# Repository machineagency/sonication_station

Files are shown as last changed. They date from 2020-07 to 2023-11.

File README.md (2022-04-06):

If you're looking for a standard operating procedure, check out the [quickstart](docs/quickstart.md).

## Intro
This project wraps a python interface around the existing Duet 3 Socket Interface, turning Jubilee into a plate handling lab automation device for sonication.

## Connecting to Jubilee
There are two ways to connect to Jubilee and execute code: (1) locally and (2) with a separate PC over a network connection.

They look like this:

### Local Connection
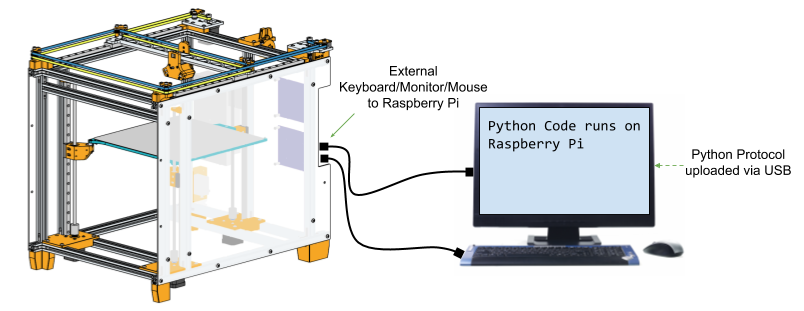
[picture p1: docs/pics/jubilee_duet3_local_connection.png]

In this mode, the Python protocol runs on the Raspberry Pi attached to the machine. It is recommended for production use.

### Closed Network Connection
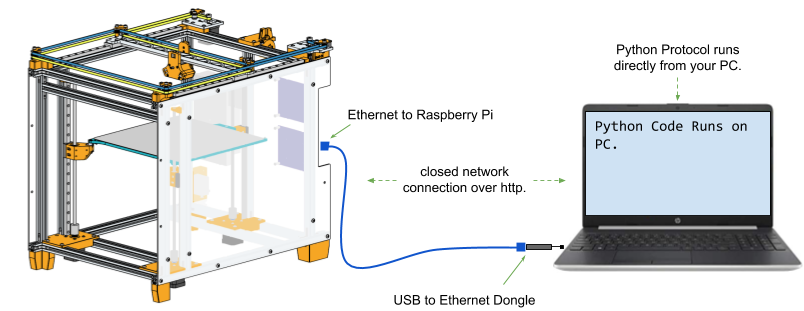
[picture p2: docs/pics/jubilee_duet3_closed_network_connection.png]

In this mode, the Python protocol runs on a separate pc with this software package installed. It is useful for testing but not recommended for production.

When running the machine in this mode, note that turning off your PC or losing the network connection will halt the machine mid-execution.
Furthermore, a laggy network connection will cause the machine to lag.
To avoid these issues in production, we recommended that running the protocol locally (on the Raspberry Pi) instead of using an arbitrary PC on the same network.

## Installation
If you are running this code locally, clone this repository onto Jubilee's attached Raspberry Pi. If you are running it over a network connection, clone it onto your PC.

Then, from within this directory (the one with this README in it), install the project via pip with ....
```
pip3 install -e .
```

Now you can spin up a connection to Jubilee by importing the driver.

## Conventions
Looking top-down at the plate, plates are indexed as follows:

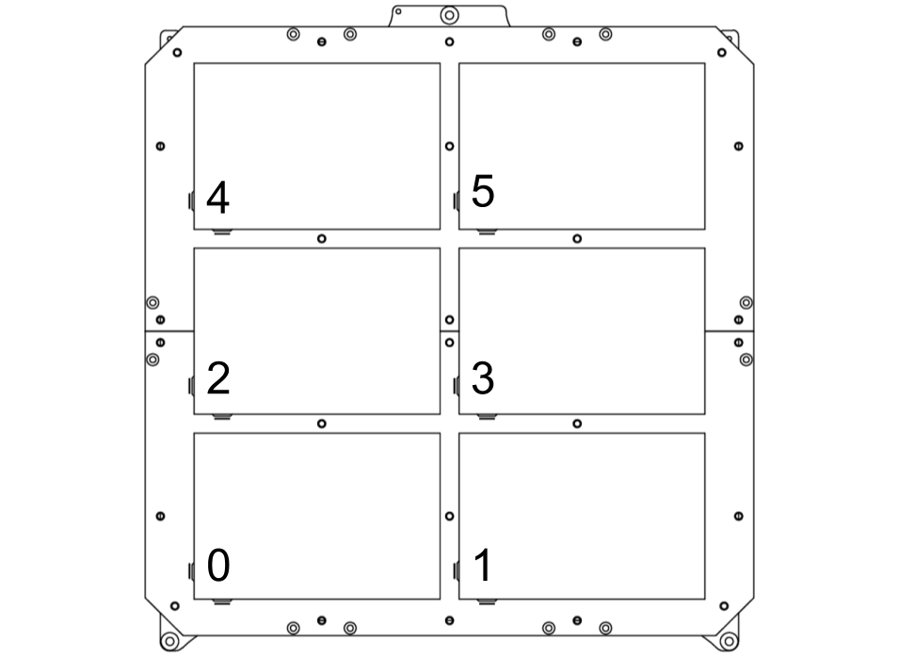
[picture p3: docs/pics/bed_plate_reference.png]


### Starting Machine State
When Jubilee is first powered up, it will need to first home all axes. You must issue this command yourself. To home, the deck must be clear of all labware.
After homing, you may populate the deck and execute protocols can be run. You only need to home once when Jubilee is first turned on, or once after any situation where the machine has lost it's position (from an event like a crash).

### Machine Pre-Protocol Setup
Once the machine is homed, you can then load labware into the machine. You will need to configure the machine with the labware you add. This can be done interactively in **prompt mode** with the *setup_plate* command. After configuring, the deck configuration can be saved to a file. If the same labware is used for a different protocol, you can reuse this file instead of reconfiguring the deck.

### Ending Machine State
All tools must be put away before Jubilee is powered off. This is the default behavior if you run the code inside a *with* statement. In any situation where the Jubilee was powered off in an emergency, you must remove any active tools on Jubilee's carriage before powering it back on.

## API
There are 3 ways of interacting with the machine:
(1) directly through a python script,
(2) interactively through a command prompt, and
(3) procedurally with predefined protocol.

## Python Script Mode
After installing this package with pip, you should be able to simply import it in python:

If you are running the code locally, the code will look like this:
```python
from sonication_station.sonication_station import SonicationStation
with SonicationStation() as jubilee:
    jubilee.sonicate_well(0, 'A', 0, 3, 10, False)
```
If you are running the code over a network from a separate PC, the code may look like this:
```python
from sonication_station.sonication_station import SonicationStation
with SonicationStation(address="192.168.1.2") as jubilee:
    jubilee.sonicate_well(0, 'A', 0, 3, 10, False)
```
Here the above *address* argument is the ip address of Jubilee as it appears on your network.

## Prompt (Maintenance) Mode
You can interactively control Jubilee through a custom prompt.
To interact with the prompt, spin it up from the python shell with:

```python
from sonication_station.sonication_station import SonicationStation
with SonicationStation() as jubilee:
    jubilee.cmdloop()
```

or, from the command line:

```
sudo path/to/sonication_station/sonication_station.py
```

This will drop you into an interactive prompt that looks like this:
```

  ____              _           _   _               ____  _        _   _             
 / ___|  ___  _ __ (_) ___ __ _| |_(_) ___  _ __   / ___|| |_ __ _| |_(_) ___  _ __  
 \___ \ / _ \| '_ \| |/ __/ _` | __| |/ _ \| '_ \  \___ \| __/ _` | __| |/ _ \| '_ \ 
  ___) | (_) | | | | | (_| (_| | |_| | (_) | | | |  ___) | || (_| | |_| | (_) | | | |
 |____/ \___/|_| |_|_|\___\__,_|\__|_|\___/|_| |_| |____/ \__\__,_|\__|_|\___/|_| |_|
                                                                                     

>>> 

```
This mode lets you input commands one at a time.

In this mode you can:

* home the machine
* execute movement commands
* execute sonication commands
* pickup and park tools
* interactively set the location/type of a new well plate
* control the machine with the keyboard arrow keys
setup the machine and execute commands serially. This interface is useful for adding to the plate inventory.

To see the list of supported commands, press TAB twice. This mode also supports TAB completion, that is, if you start typing a command and press TAB twice, the prompt will either attempt to auto-complete any possibilities or show you a list of possible completions.
To get help on any command, simply type:

```
>>> help command_name_here
```

## Protocol Mode
This method is for invoking predefined protocol. Protocol mode may be useful for generating a series of plate operations programmatically from another program and then simply executing them on the Sonication Station. Protocols consist of a series of sonication commands executed sequentially.

Running the machine in protocol mode is simply a matter of telling the machine to read a predefined protocol file.
```python
# Assume that Jubilee is both homed and populated with the correct labware for this protocol.
from sonication_station.sonication_station import SonicationStation
with SonicationStation() as jubilee:
    jubilee.execute_protocol_from_file("/path/to/protocol_file.json")
```

### Protocol API
Under the hood, a protocol file is a json file. A sample protocol looks like this:
```json
{
   "protocol": [
       {
           "operation": "sonicate_well",
           "specs": {
               "deck_index": 5,
               "row_letter": "A",
               "column_index": 1,
               "plunge_depth": 10.0,
               "seconds": 3.0,
               "autoclean": false
           }
       },
       {
           "operation": "sonicate_well",
           "specs": {
               "deck_index": 5,
               "row_letter": "A",
               "column_index": 2,
               "plunge_depth": 10.0,
               "seconds": 3.0,
               "autoclean": false
           }
       }
   ]
}
```
Here, the protocol contains one important field *protocol*, which is a list of operations that will be executed sequentially.
So far, only one operation **sonicate_well**, is implemented. the options are as follows:
* **deck_index:** the deck index of the plate
* **row_letter:** the row index on the plate, indicated by letter
* **column_index:** the column indicated by integer
* **plunge_depth:** the depth to plunge the sonicator into the glassware as measured from the top of the glassware
* **seconds:** time in seconds to run the sonicator
* **autoclean**: (boolean), whether or not to run a predefined cleaning protocol.

Note that if **autoclean** is set to true, a cleaning protocol must be defined in the machine configuration. Cleanin protocols can also be defined in prompt mode.

## Deck Configuration
Before running a protocol, Jubilee's deck must be configured with the labware that the protocol needs. Specifically, Jubilee needs to know:
* for each piece of labware
    * the well count (12 \[scintillation vile holder\], 48, 96, etc)
    * the XY location of the labware
    * the deck slot number
    * the height of the labware
* a minimum height at which all tools can safely travel over all labware currently loaded on the deck (the *safe_z* height).

This configuration must be done in **prompt mode**.

### Safe Z Height
The *safe_z* height is the height at which the tip of any tool can safely clear the tallest labware without crashing into it. It is defined in mm as the distance of the active tool tip and the deck plate surface.

If the machine is homed, you can measure the current tool tip height by issuing the *position* command.
```
>>> position
[150.0, 150.0, 65.0]
>>> 
```
Here the XYZ coordinates are 150, 150, 65mm respectively.

You set the *safe_z* height in **prompt mode** like so:
```
>>> safe_z z=65
```

You can read back the *safe_z* by simply entering *safe_z* without arguments
```
>>> safe_z
65
>>>
```

### Plate Setup
You can add a piece of labware into Jubilee's configuration by running the *setup_plate* command. This will drop you into an interactive session where the machine will walk you through the setup.

When the machine is configured, you can save your configuration to a file with *save_deck_configuration*. That way, you can run the same protocol again without having to redo this (somewhat tedious) setup.

### Acknowledgements
This work was partially supported by the  University of Washington (UW) Molecular Engineering Materials Center (MEM-C)

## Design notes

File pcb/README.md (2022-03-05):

# Sonicator PCB

This PCB attaches on top of the Raspberry Pi enabling its GPIOs to control the Sonicator.

## Fabrication

To make this pcb, you'll need to send files (usually gerbers) out to a PCB Fab house of your choice.
Here are some options:

* [OSH Park](https://oshpark.com/) will actually natively accept **.kicad\_pcb** files directly. (This is probably the easiest option.)
    * [instructions for gerber generation](https://docs.oshpark.com/design-tools/kicad/generating-kicad-gerbers/)
* [PCBWay](http://pcbway.com/)
    * [instructions for gerber generation](https://www.pcbway.com/blog/help_center/Generate_Gerber_file_from_Kicad.html)
* Bay Area Circuits has a No-Silk-No-Soldermask 24-hour [Bare Bones Special](https://bayareacircuits.com/prototype-printed-circuit-boards-pcbs/) for time crunched prototypes.

## Assembly

This PCB can be assembled by hand with some tweezers, a microscope (or cheap microscope webcam), and, optionally, a stencil.
Parts will need to be ordered from the BOM.
(You can regenerate the BOM from the native Kicad files.)

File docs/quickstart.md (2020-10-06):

# Quickstart

The General Standard Operating Procedure for running a protocol on Jubilee:

## Standard Operating Procedure for Production Use
Assumes procedures will run locally on the attached Raspberry Pi.

1. Power on the machine without labware
1. Home the machine
1. If code was written elsewhere, upload it to the machine with a USB drive.
1. Configure the deck plate or use an existing deck plate configuration file.
1. Populate the deck with labware
1. Either:
    1. Execute one or more sonication operations in manual mode
    1. Execute one or more python scripts
    1. Execute one or more json protocol files
1. Ensure that all tools are put away
1. Remove all labware from the machine
1. Power off the machine

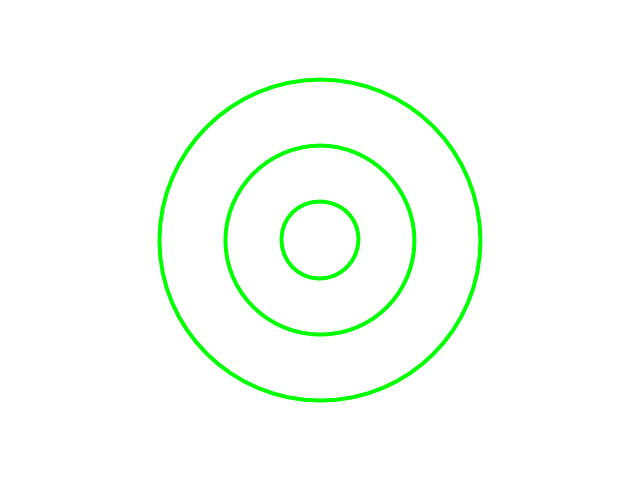
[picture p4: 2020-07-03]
sonication_station/web_video_feed/overlay.png

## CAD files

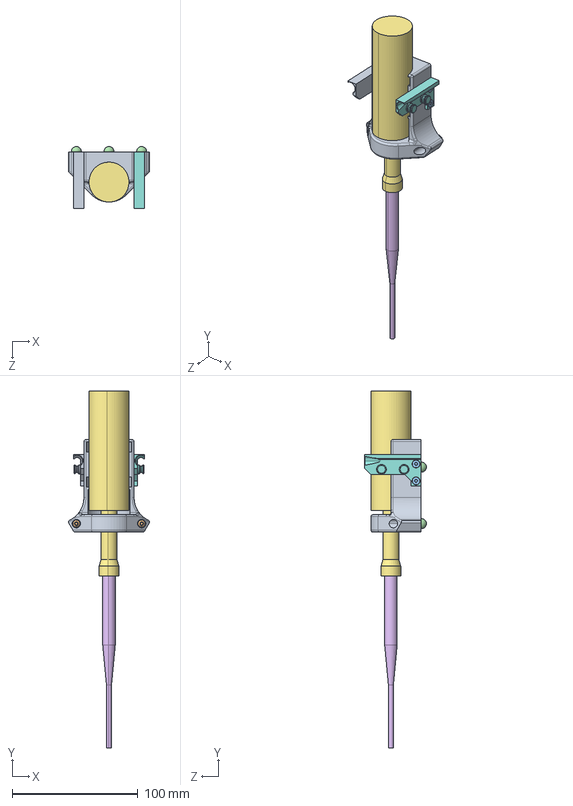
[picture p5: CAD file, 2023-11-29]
tools/q125_sonicator_tool/step/sonicator_tool_assembly.STEP
64.4 x 284.1 x 49.3 mm
sonicator_base_tool_plate_tool plate
wedge_plate
m3_6mm_flathead_screw_92125A126_92125A126 x 7
m3_threaded_ball x 3
m3_heat_set_insert_94180A331_94180A331 x 3
q125_sonicator_head
sonicator_tool_wing_Standard Right Tool Wing
sonicator_tool_wing_Standard Left Tool Wing
m3_6mm_buttonhead_screw_92095A179_92095A179 x 3

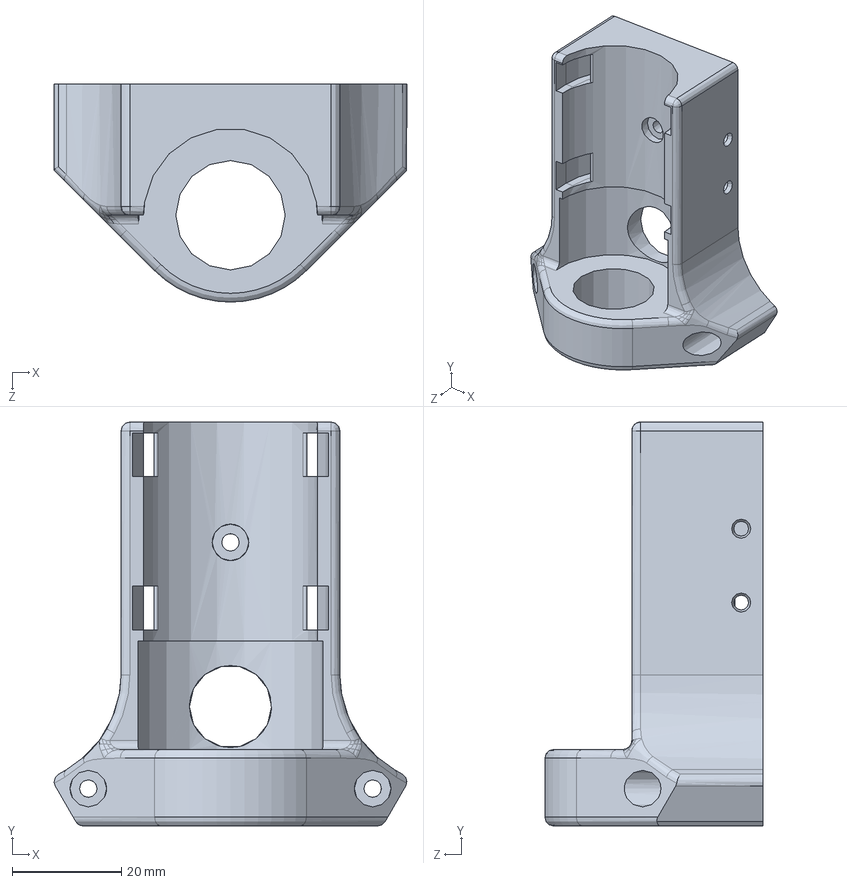
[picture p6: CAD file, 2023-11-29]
tools/q125_sonicator_tool/solidworks/sonicator_base_tool_plate.SLDPRT
64.5 x 73.8 x 39.9 mm

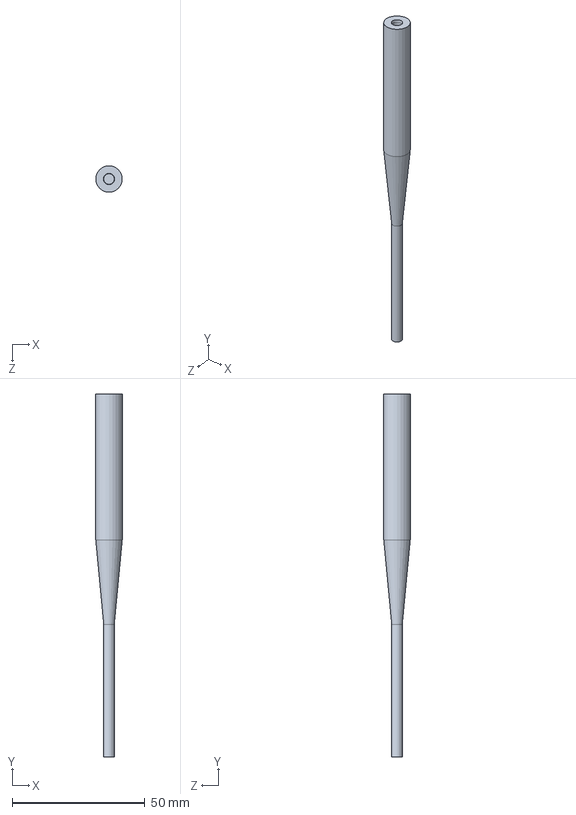
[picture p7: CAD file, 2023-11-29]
tools/q125_sonicator_tool/solidworks/q125_sonicator_head.SLDPRT
10.0 x 136.8 x 10.0 mm

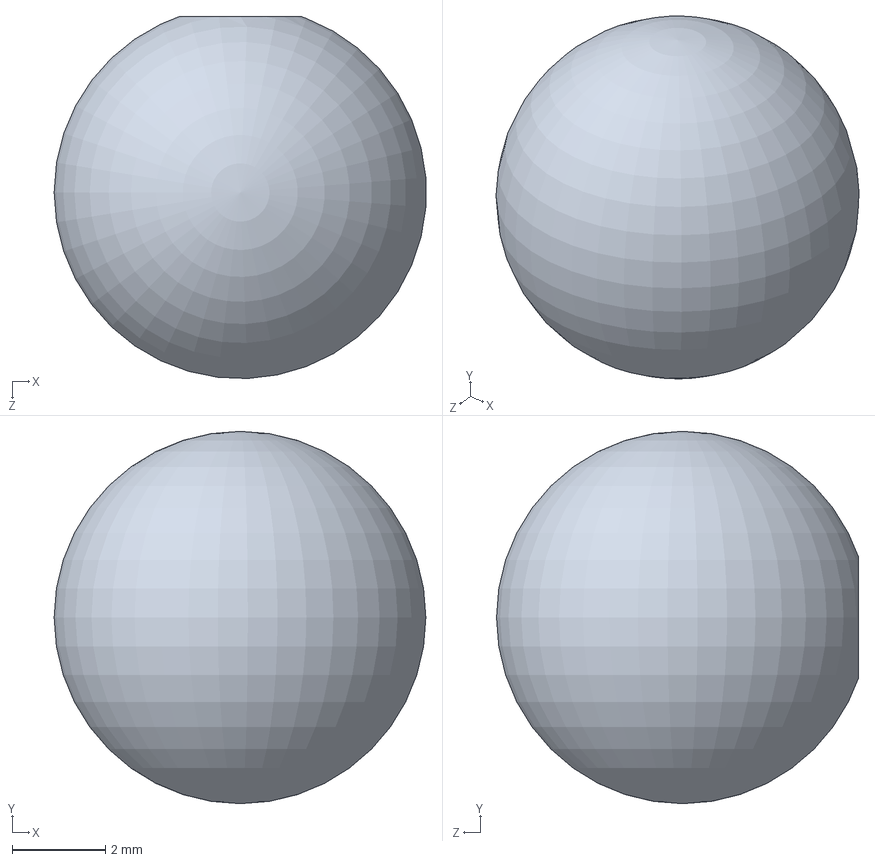
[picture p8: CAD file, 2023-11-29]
tools/q125_sonicator_tool/solidworks/m3_threaded_ball.SLDPRT
7.99 x 8.00 x 7.78 mm

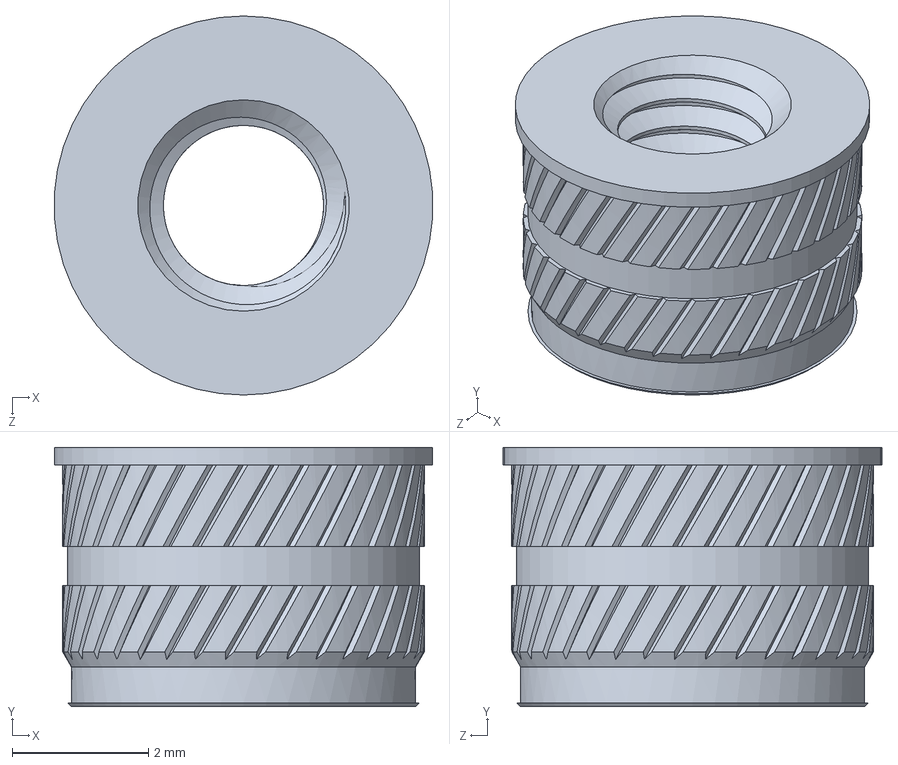
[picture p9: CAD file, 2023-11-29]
tools/q125_sonicator_tool/solidworks/m3_heat_set_insert_94180A331.SLDPRT
5.55 x 3.80 x 5.56 mm

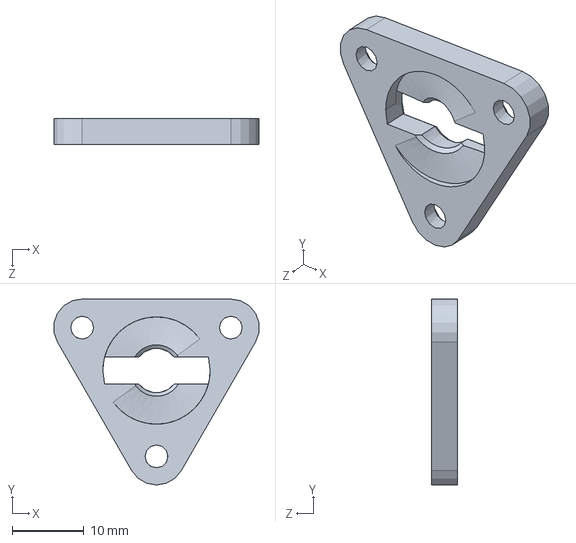
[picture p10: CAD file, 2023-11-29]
tools/q125_sonicator_tool/solidworks/wedge_plate.SLDPRT
28.7 x 26.0 x 3.60 mm

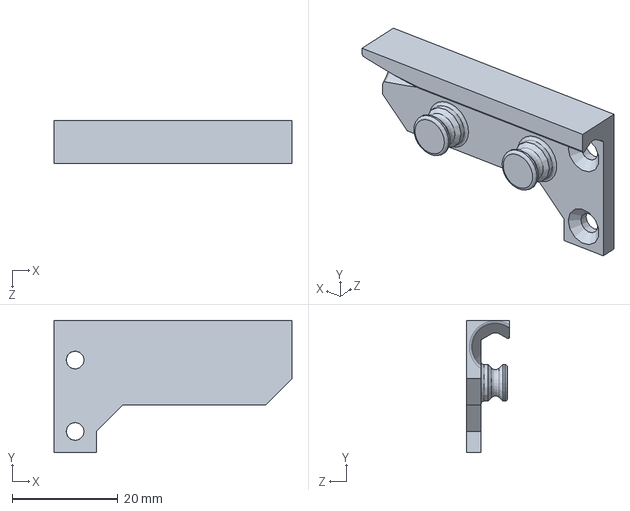
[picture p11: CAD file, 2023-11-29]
tools/q125_sonicator_tool/solidworks/sonicator_tool_wing.SLDPRT
45.0 x 25.0 x 8.20 mm

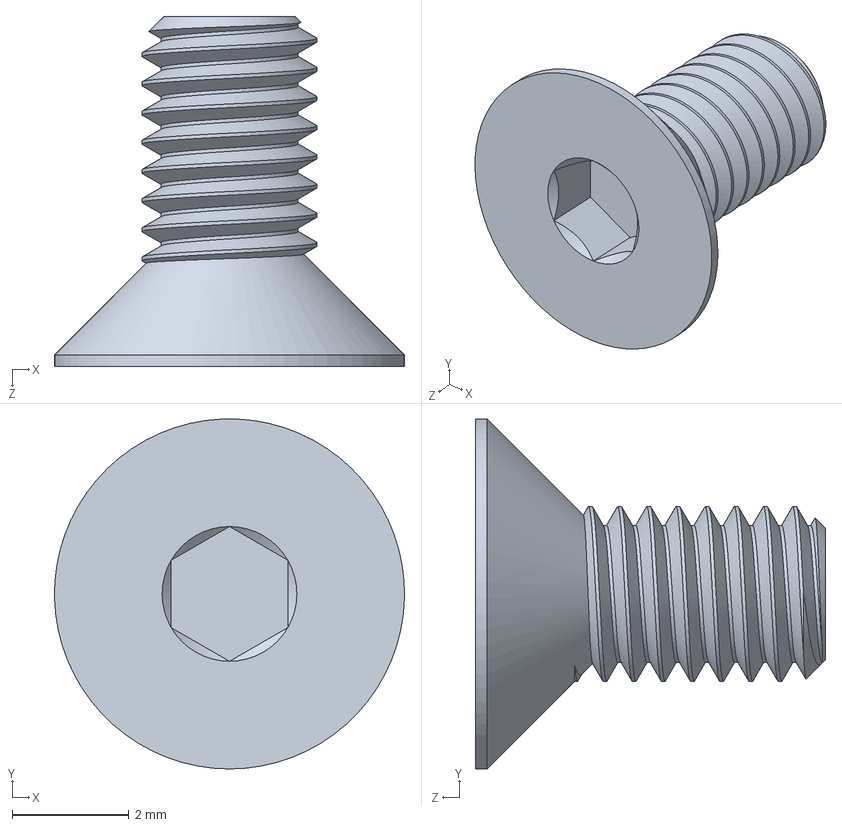
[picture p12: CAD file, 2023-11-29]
tools/q125_sonicator_tool/solidworks/m3_6mm_flathead_screw_92125A126.SLDPRT
6.00 x 6.00 x 6.00 mm

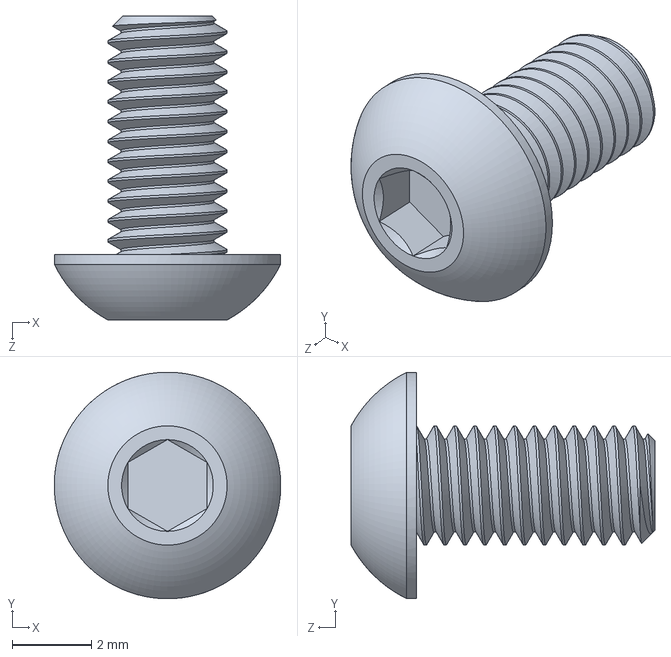
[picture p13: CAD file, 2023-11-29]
tools/q125_sonicator_tool/solidworks/m3_6mm_buttonhead_screw_92095A179.SLDPRT
5.70 x 5.70 x 7.65 mm

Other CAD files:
tools/q125_sonicator_tool/solidworks/sonicator_tool_assembly.SLDASM

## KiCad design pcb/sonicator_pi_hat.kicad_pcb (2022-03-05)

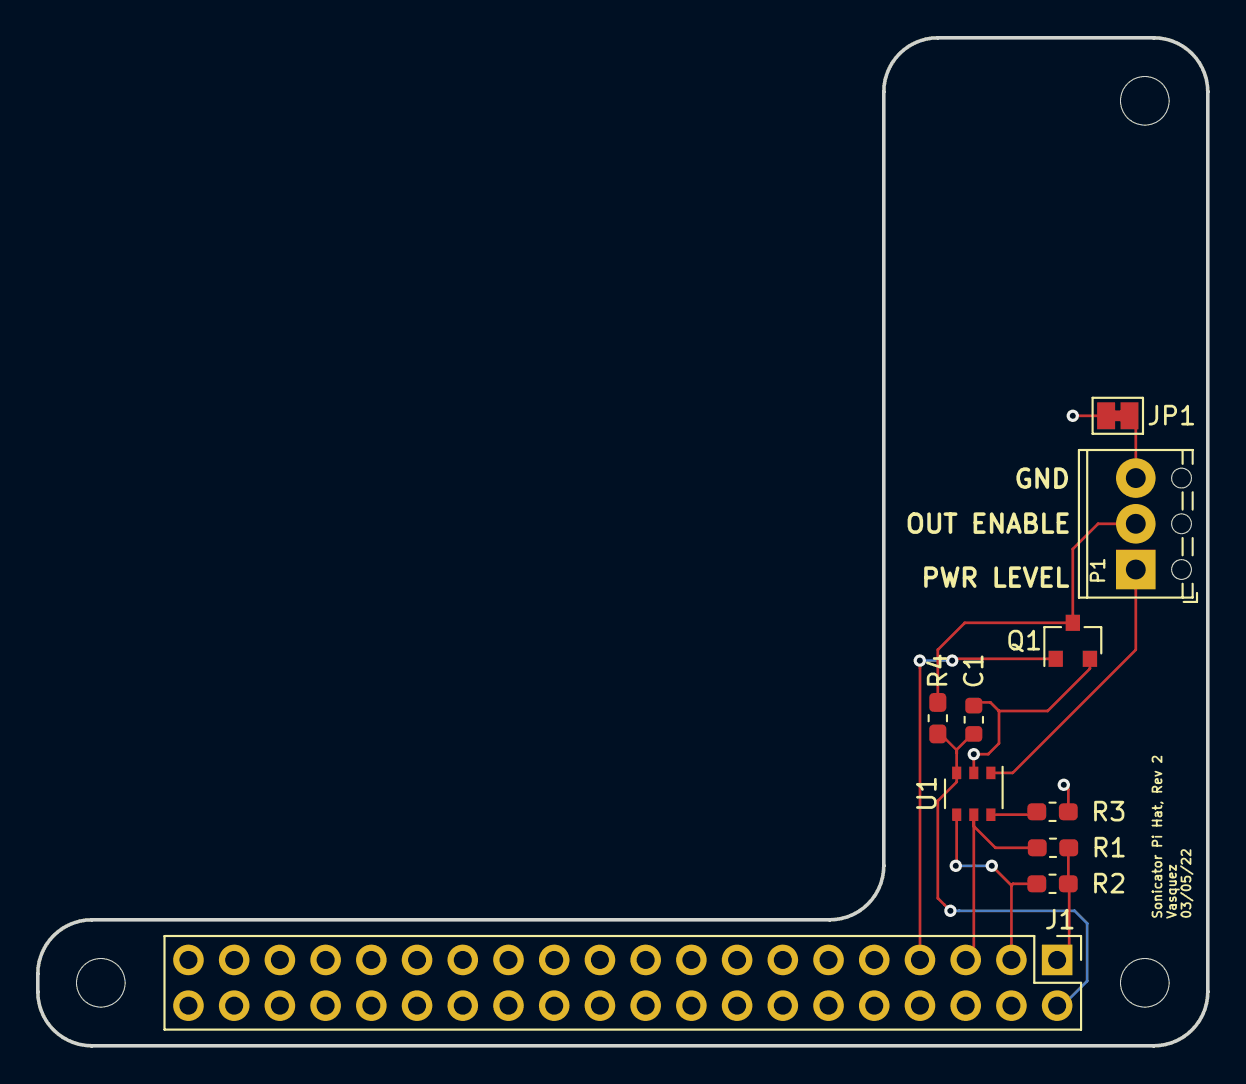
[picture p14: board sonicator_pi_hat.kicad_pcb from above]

Board: 2 copper layers, 65.0 x 56.0 mm, 10 parts (0 on the bottom side), 10 nets.

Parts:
C1: 1uF; C_0603_1608Metric
J1: Raspberry_Pi_2_3; PinHeader_2x20_P2.54mm_Vertical
JP1: Jumper; SolderJumper-2_P1.3mm_Bridged_Pad1.0x1.5mm
P1: 3pos_terminal_block; TerminalBlock_Phoenix_MPT-0,5-3-2.54_1x03_P2.54mm_Horizontal
Q1: 2N7002; SOT-23
R1, R2, R4: 4k7; R_0603_1608Metric_Pad1.05x0.95mm_HandSolder
R3: 10k; R_0603_1608Metric_Pad1.05x0.95mm_HandSolder
U1: MCP4725; TSOP-6_1.65x3.05mm_P0.95mm

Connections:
+3V3: J1.1 (3V3), R1.1, R2.1
+5V: C1.1, J1.2 (5V), R4.1, U1.3 (VDD)
/OUTPUT_ENABLE: P1.2, Q1.3 (D), R4.2
/OUTPUT_PWR_LEVEL: P1.1, U1.1 (VOUT)
GND: C1.2, J1.6 (GND), J1.9 (GND), J1.14 (GND), J1.20 (GND), J1.25 (GND), J1.30 (GND), J1.34 (GND), J1.39 (GND), JP1.1, Q1.2 (S), R3.2, U1.2 (VSS)
GNDPWR: JP1.2, P1.3
unnamed: J1.3 (SDA/GPIO2), R2.2, U1.4 (SDA)
unnamed: J1.5 (SCL/GPIO3), R1.2, U1.5 (SCL)
unnamed: J1.7 (GCLK0/GPIO4), Q1.1 (G)
unnamed: R3.1, U1.6 (A0)

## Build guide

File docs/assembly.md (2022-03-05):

# Machine Assembly

Transforming Jubilee into the Sonication Station requires the addition of some custom hardware and software beyond building the frame.

## Hardware Checklist

### Single Board Computer for SBC Mode
* 32GB SD card
* Raspberry Pi 4, 4GB
* ethernet cable
* [ethernet-to-usb3 adapter](https://www.amazon.com/gp/product/B00M77HMU0)

### Sonicator Tool
* Q125 Sonicator Horn
* Sonicator Probe (various probe sizes, including pn: 4423, pn: 4422, and pn: 4435)
* Sonicator Control PCB, pn: KITVC1025 (20kHz) or pn: KITVC1045 (40kHz)
* Sonicator Wiring Harness
    * 1x [Molex: 0022552102](https://www.digikey.com/en/products/detail/molex/0022552102/303176)
    * 3x [Molex: 0016020086](https://www.digikey.com/en/products/detail/molex/0016020086/467788)
    * 1x [McMaster-Carr: 7243K117](https://www.mcmaster.com/7243K117/) for the sonicator horn wiring
    * 1x [McMaster-Carr: 7243K122](https://www.mcmaster.com/7243K122/) for the sonicator horn wiring

### Camera Tool
* [Sonicator Pi Hat PCB](./pcb)
* [Arducam Lens Board](https://www.amazon.com/gp/product/B013JTY8WY)
* [HDMI Cable](https://www.amazon.com/gp/product/B00Z07JYLE) (flexible, 2m or 6ft)
* [Arducam CSI to HDMI Cable Extension Module](https://www.amazon.com/gp/product/B06XDNBM63)

## Overall Setup

Jubilee will be provisioned in "SBC Mode" and the sonication\_station python package in this repository will be installed on it.
The Sonicator Pi Hat will be attached to the Pi and connected to the Sonicator Control PCB.

## Diagram HERE

## Assembly Instructions
1. Order and populate the [Sonicator Pi Hat](./pcb) PCB.
1. Order the Parts for a Sonicator Tool and a Camera Tool.
1. Install [DuetPi](https://docs.duet3d.com/en/User_manual/Machine_configuration/SBC_setup) OS on the Raspberry Pi
1. Assemble the Sonicator Tool and harness and the camera tool and harness.
1. Connect to the Raspberry Pi, give it internet access, and install the sonication\_station package according to the [instructions](https://github.com/machineagency/sonication_station#installation)
1. Set the XYZ Tool Offsets of the Sonicator and and Jubilee Tool.

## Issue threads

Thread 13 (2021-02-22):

### ISSUE TITLE
Autocleaning needs to have power option exposed during setup_autoclean_protocol

### ISSUE THREAD

**Issue by Antonedw** [machineagency/sonication_station#13]
Expose power option as an input when using **prompt mode**  else leads to error due to missing argument when running protocol.

**Comment by Poofjunior** [comment]
also implemented in this branch. Needs testing.
https://github.com/machineagency/sonication_station/tree/dev/duty_cycle_sonication

**Comment by Poofjunior** [comment]
Ok this looks good!

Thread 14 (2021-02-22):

### ISSUE TITLE
Sonication horn remains on after KeyboardInterrupt in Prompt Mode

### ISSUE THREAD

**Issue by Antonedw** [machineagency/sonication_station#14]
When interrupting a protocol running in prompt mode the sonication horn stays on after the keyboard interruption. The horn stays on to the same setting that was present during the keyboard interruption. Currently, the only way to stop the horn is to turn the entire machine on and off completely.

**Comment by Poofjunior** [comment]
Ok; this looks like it should be a quick fix. Changes are up here in a branch that I should be able to test before the end of the weekend.
https://github.com/machineagency/sonication_station/tree/dev/sonicator_safe_exit

**Comment by Poofjunior** [comment]
Ok this should now be fixed.

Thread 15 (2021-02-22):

### ISSUE TITLE
Duty cycle for sonication horn not present

### ISSUE THREAD

**Issue by Antonedw** [machineagency/sonication_station#15]
The option of the duty cycle is not present as an argument to sonicate_well(). At the moment, a duty (ratio on/off) cycle is achievable by just calling the horn to run in another well, however, the power option to zero or a pause feature is needed.

**Comment by Poofjunior** [comment]
Ok, also implemented, but needs to get tested later.
https://github.com/machineagency/sonication_station/tree/dev/duty_cycle_sonication

**Comment by Poofjunior** [comment]
Ok, this is now implemented. When you run it, you'll get a print message when the sonicator turns on and off. (We can get rid of this if you want.)
```
>>> sonicate_well 0 A 0 15 2.5 1 1 2 autoclean=False
Moving to: (264.055, 200.000)
Sonicating for 2.5 seconds!!
0.00 | Sonicator on.
2.00 | Sonicator off.
2.00 | Sonicator on.
2.50 | Sonicator off.
2.50 | Finished sonicating.
done!
Moving to: (124.250, 79.750)
Sonicating for 3.0 seconds!!
0.00 | Sonicator on.
0.50 | Sonicator off.
1.00 | Sonicator on.
1.50 | Sonicator off.
2.00 | Sonicator on.
2.50 | Sonicator off.
3.00 | Finished sonicating.
done!
Moving to: (96.167, 79.750)
Sonicating for 3.0 seconds!!
0.00 | Sonicator on.
0.50 | Sonicator off.
1.00 | Sonicator on.
1.50 | Sonicator off.
2.00 | Sonicator on.
2.50 | Sonicator off.
3.00 | Finished sonicating.
done!
```

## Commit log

2020-06-21 updating completion to print in columns
2020-07-04 launching/killing camera feed works
2020-07-05 adding general case toolchange macros for tools with very different heights
2020-07-11 got sleep-until-next-thread-update working
2020-08-11 hid extraneous camera output
2020-08-27 camera pickup turns on camera
2020-11-06 exposing sonicator power level
2020-12-02 exposing power level for config mode.
2022-03-05 adding kicad pcb files.
    [sonicator_pi_hat.kicad_pcb, sonicator_pi_hat.kicad_sch]
2022-03-05 schematic and instructions update
    [sonicator_pi_hat.kicad_sch]
2022-03-05 adding high level assembly instructions
2022-04-06 updating config for current generation of jubilee motors
2023-11-29 add sonicator solidworks and step files
    [m3_6mm_buttonhead_screw_92095A179.SLDPRT, m3_6mm_flathead_screw_92125A126.SLDPRT, m3_heat_set_insert_94180A331.SLDPRT, m3_threaded_ball.SLDPRT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]
